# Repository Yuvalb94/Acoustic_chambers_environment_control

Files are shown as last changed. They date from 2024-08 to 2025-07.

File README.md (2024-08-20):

# Acoustic chamber environment control setup
In our experiments we house birds in acoustic chambers. These chambers include wide spectrum LEDs to mimmick sun light and a fan system to circulate fresh air in the chamber. Seasonal birds, like the canaries we study, are sensitive to the daily cycle of light and dark, the photoperiod, and to its changes as days grow longer in spring and grow shorter in autumn. To mimmick this in the acoustic chambers, we created the environment control and monitoring setup described in this repository. This setup, called *environmental system* and sketched in figure 1, controls the light switch in up to 8 acoustic chambers, monitors the light level, humidity, and temperature in a sentinel chamber, and monitors the weight of up to 8 birds using [in-house built scales](https://github.com/NeuralSyntaxLab/acoustic_chamber_environment_control/blob/scale_system_yc_version/scale_system_documentation/scale_design.md).
## System overview
Figure 2 shows the *environmental system*'s functional overview. The system is controlled by a python script running on a Raspberry Pi computer. [This script](https://github.com/NeuralSyntaxLab/acoustic_chamber_environment_control/blob/main/arduino_main.py) communicates with an Arduino microcontroller, which controls light switches, reads sensor data, and sends information back to the Raspberri Pi. 

The Raspberry Pi script:
 * Determines when lights should be turned on/off according to user-defined photoperiod regimes (detailed in [Operations](https://github.com/NeuralSyntaxLab/acoustic_chamber_environment_control/blob/scale_system_yc_version/README.md#operations)) and sends on/off commands to the Arduino.
 * Receives a sentinel chamber's temprature, humidity, and light sensor data from the Arduino and stores it and in .csv files.
 * Receives weight data of birds that are being monitored from the arduino and stores it (also in .csv files).
 * Store data locally and on the [storWIS drive](https://github.com/NeuralSyntaxLab/lab-handbook/wiki/Lab-Operations-and-Procedures#storwis) and/or send the data to the experimenter via Slack or Email.

Our environmental system allows flexibility in determining the photoperiod and its changes across days. Each  *environmental system* is given its unique ID. This allowes running experiments in different light cycles, or experiments on more than 8 acoustic chambers .

<figure>
 <br>
<figcaption> Figure 1: The environmental system setup </figcaption>
</figure>

---

## Table of contents
* **Part list** 
* **Preperations**
  1. [Setting up the Raspberri Pi](#setting-up-the-raspberry-pi)
  2. [Preparing hardware and connecting to Arduino](#preparing-hardware)
  3. [Setting up Arduino](#setting-up-arduino)
* **Operations**
  1. [Light control mode](#light-control-mode)
  2. [Light control & data acquisition mode](#light-control--data-acquisition-mode)

<br>

## Part list
[This table](https://github.com/NeuralSyntaxLab/acoustic_chamber_environment_control/blob/scale_system_yc_version/parts%20list.xlsx) contains the part list required to constructing one *environmental system*. The list reflects our current choice of microcontroller models, wiring, and connections. Many of these can be switched for the convenience of the user and their specific needs.

## Preperations
This section is a general overview of how to construct the *environmental system*. It contains links to separate manuals for manufacturing system components and describes how to connect them. This section also contains instructions about how to upload the Arduino code and how to calibrate the scale system. The next section, Opertaions, describes how to use the system once it's constructed and calibrated. 

### System hardware components
The following hardware components are constructed separately and wired after their installation in the acoustic chambers or in the experiment room's main instrumentation rack:
1. A Raspberry Pi minicomputer.
2. An Arduino Uno microcontroller.
3. Light control system - consists of 1 control box which connects to relay swiches on a maximum of 8 acoustic chambers.
4. Sensor box - consists of a humidity & temprature sensor (DHT) and a photoresistor (light sensor). Up to 1 box per setup.
5. Scale system - consists of 1 control box, capable of connecting up to 8 scales. Up to 1 system per setup.

To demonstrate the functional operation of the system, Figure 2 shows a simplified schematic that illustrates how sensors and actuators are connected to the Arduino microcontroller.
<figure>
  
  <br>
  <figcaption>Figure 2: Schematic diagram of the system components and their connections</figcaption>
</figure>

<br>
<br>
The following sequence of steps should be taken to construct the hardware components and to calibrate the system:

### 1. Set up the Raspberry Pi
When using a new Raspberry Pi, it has to undergo several steps, described in the [configuration guide](https://github.com/NeuralSyntaxLab/acoustic_chamber_environment_control/blob/cf7c2d09ca352680ac4c0b2b953d89da0c118fb5/User%20Guides/Raspberry%20Pi%20Configuration.md), before using it to operate the environmental system. 

If you are using an already used Raspberry Pi, move on to preparing the hardware.
Return to the [configuration guide](https://github.com/NeuralSyntaxLab/acoustic_chamber_environment_control/blob/cf7c2d09ca352680ac4c0b2b953d89da0c118fb5/User%20Guides/Raspberry%20Pi%20Configuration.md) if issues arise when running the `control_main.py` script.

### 2. Manufacture and prepare the light switches and sensor box 
This [assembly guide](https://github.com/NeuralSyntaxLab/acoustic_chamber_environment_control/blob/cf7c2d09ca352680ac4c0b2b953d89da0c118fb5/User%20Guides/Hardware%20Assembly%20Guide.md) contains a step-by-step manual explaining how to build each device.

* #### 2.1 The light control system
Figure 3a illustrates the light control system. The system contains relay switches to control the light in each acoustic chamber and a control hub-box (3b) that transmitts the Arduino command to all the individual switches. The hub-box contains two output ports on the short edge that are used to connect to the Arduino microcontroller and a 5V external power source. On the long edge on both sides are 8 output ports that can connect to the relay switches on the acoustic boxes. To connect each relay switch to the hub, construct the cable shown in Figure 3c.

<figure>
  <div style="display: flex; justify-content: space-around; align-items: center;">
    <div>
      
      <figcaption style="text-align: center;">3a; Light control system diagram</figcaption>
    </div>
    <div>
      <br>
      <br><figcaption style="text-align: center;">3b; Light control hub-box.<br>The Arduino port connects the signal circuit, which transmits the signal from the Arduino to all relay switches, along with a 'GND' connection. The 5V port connects to an external 5V power source that helps send voltage to the relay switches without overloading the Arduino microcontroller.</figcaption>
    </div>
    <div>
    <br>
    <br><figcaption style="text-align: center;">3c; Light control communication cable.<br>The cable is a simple 4-core cable with a 3-PIN Pigtail connector for easily connecting to the hub-box on one end, and a 3-pos connector to fit on the relay module on the other. In order to connect the relay switches on each acoustic box to the control hub, connect the relay-module end of the cable to the switch (as shown in the figure), spread the cable conveniently to the instrumentation rack and connect to one port of the hub-box.</figcaption>
    </div>
  </div>
</figure>

* #### 2.2 The sensor box
The sensor box should look like this: <br>
<figure>
   <br>
  <figcaption>Figure 4: The sensor box</figcaption>
</figure>
<br>

The box contains:

* DHT sensor (for detecting humidity, temprature)
* Photoresistor (for detecting light intensity)
* A connector for the communication cable (for receiving voltage - red and black wires, and sending data - green for DHT, white for photoresistor)

In order to connect the sensor box to the setup, construct the communication cable, shown in Figure 5 (guide for making the cable [here](https://github.com/NeuralSyntaxLab/acoustic_chamber_environment_control/blob/cf7c2d09ca352680ac4c0b2b953d89da0c118fb5/User%20Guides/Hardware%20Assembly%20Guide.md)).

<figure>
  <br>
  <figcaption>Figure 5: The cable for connecting the sensor box to the Arduino</figcaption>
</figure>

### 3. Manufacture and calibrate the scale system
The scale system allows to measure the weight of 8 birds simultaneously. This [Scale System setup guide](https://github.com/NeuralSyntaxLab/acoustic_chamber_environment_control/blob/7b98ca46d210fc865f576b8630c2cdef0f82fe2f/User%20Guides/Scaling%20System%20Setup%20Guide.md) explains how to build the system and how to calibrate the scales for getting precise measurements. **Note:** Calibrating the scale system requires connecting it the Arduino and running the Arduino code [described below](https://github.com/NeuralSyntaxLab/acoustic_chamber_environment_control/blob/scale_system_yc_version/README.md#5-set-up-the-arduino). 

Figure 6 illustrates the whole scale system. Similar to the light control system, it contains a control hub-box, which contains special breakout boards (Qwiic Scale NAU7802, Qwiic MUX) that helps transmit, amplify and convert the signal from up to 8 scales simultaneously. The Qwiic MUX board inside the hub-box connects to the Arduino microcontroller on one end, and the NAU7802 board connects to the eight input ports to which we can connect the scales with long communication cables.

<figure>
  <div style="display: flex; justify-content: space-around; align-items: center;">
    <div>
      
      <figcaption style="text-align: center;">6a; Scale system illustration.</figcaption>
    </div>
    <div>
      <br>
      <br><figcaption style="text-align: center;">6b; Scale system control hub-box.<br>The box contains the breakout boards that are connected to the Arduino and the docking ports. On the side of the box, channel numbers are marked for each port, so that it fits the channel on the Qwiic MUX that it is connected to.</figcaption>
    </div>
    <div>
    <br>
    <br><figcaption style="text-align: center;">6c; Scale system control communication cable.<br>The cable is a simple 4-core cable with a 4-PIN Pigtail connector for easily connecting to the hub-box on one end, and a 4-pos connector to connect to the scale on the other. In order to connect the scales to the control hub, connect the scale end of the cable to the scale, spread the cable conveniently to the instrumentation rack and connect to one port of the hub-box.</figcaption>
    </div>
    <div>
    <br>
    <br><figcaption style="text-align: center;">6d; The scale.</figcaption>
    </div>
  </div>
</figure>

### 4. Connect all the hardware to the Arduino
In order for the Arduino microcontroller to receive the data smoothely and without failtures, the devices must be connected properly. Figure 7 schematize the wiring diagram:
<figure>
  
  <figcaption>Figure 7: The systems's wiring diagram</figcaption>
</figure>
<br>

#### Wiring list 
The colors of the lines in Figure 7 refer to different lines in the cables connecting the devices to the Arduino according to the following wiring list. Each entry in the list is formatted as "Device wire ID (function in the device) - pin on Arduino":
1. To connect the light control system (2 wires):
   * Black (ground) - to any 'gnd'
   * White (signal) - to digital channel 13

2. To connect the sensor box (4 wires):
   * Black (ground) - to any 'gnd'
   * Red (voltage) - to 5V channel
   * White (photoresistor) - to analog channel A0
   * Green (DHT) - to digital channel 8

3. To connect the Scale System (4 wires):
   * Black (ground) - to any 'gnd'
   * Red (voltage) - to 3.3V channel
   * Yellow (signal) - to 'SCL' channel
   * Blue (signal) - to 'SDA' channel

### 5. Set up the Arduino
Before running the main script on the Raspberry Pi, make sure to load the appropriate code for the operation that you want on the Arduino.

1. Connect the Arduino to the Raspberri Pi with a USB-A to USB-B cable.
2. Open the relevant arduino code:
   * [arduino_code_0](https://github.com/NeuralSyntaxLab/acoustic_chamber_environment_control/blob/scale_system_add/arduino_codes/arduino_code_0/arduino_code_0.ino) - For light control only mode.
   * [arduino_code_1](https://github.com/NeuralSyntaxLab/acoustic_chamber_environment_control/blob/scale_system_add/arduino_codes/arduino_code_1/arduino_code_1.ino) - For light control & data analysis mode.
   * [arduino_code_2](https://github.com/NeuralSyntaxLab/acoustic_chamber_environment_control/blob/scale_system_add/arduino_codes/arduino_code_2/arduino_code_2.ino) - For initial set up and calibration of the Scale System.
3. Load the relevant code onto the Arduino using the IDE. (see instructions [here](https://docs.arduino.cc/learn/starting-guide/the-arduino-software-ide)).
4. Once all the hardware components are connected to the Arduino, open 'Serial Monitor' to check that the arduino operates smoothely, acquiring the neccesary data in every mode.

## Operations

$${\color{red}\text{Begin comment ********}}$$

*This section is organized in a difficult way. Specifically, the definition of operation modes and the definition of how to configure things are intermingled and this is too confusing. I suggest a different structure below*

$${\color{red}\text{End comment ********}}$$

### Operation overview
The *environmental system* can be used in two distinct *operation modes*:
1. Light cycle only - The system controls the light switches and does not read sensors. In this mode the system **TBD: Does it save data? Does it send data to the user?**
2. Light and sensors - The system controls the lights and also reads sensors.

The user chooses the operation mode by loading different codes to the Arduino and by manupulating a single configuration file on the Raspberri Pi. This section instructs how to run the system in example cases of the two operation modes. For the full information about how to use the configuration file see [this manual](https://github.com/NeuralSyntaxLab/acoustic_chamber_environment_control/blob/scale_system_add/config_files/How%20to%20use%20the%20config%20file.md).

### To start running the system

After creating the configuration file, the user needs to edit the `startup_script.sh` shell script and point to the full path of the configuration file by changing this line: <br>
`
py_script_name="$parent_path/control_main.py --config=/path/to/repo/acoustic_chamber_environment_control/config_files/config_file_name.yaml"
` 
<br> 

Editing the `startup_script.sh` shell script is needed since the system is set to execute it automatically on start-up. This prevents light cycle failues if the system accidently boots (e.g. after a power fluctuation) to ensure minimal disruption for the animals.

Then, to start running the *environmental system* the user can:

* Boot the Raspberri Pi.
* Alternatively,
  * Open a terminal on the Raspberri Pi.
  * Change the directory to the root directory of this repository.
  * Execute the shell script `startup_script.sh`

### Day to day operations
#### 1. Changing the light cycle
#### 2. Configuring the system's reports
#### 3. Housing a new bird
#### 4. Removing a bird

### Operation modes
### *The "Light cycle only" operation mode*
This is a minimalistic operation mode that allows using the setup only for controlling the light cycle. In this mode **TBD: what will be controlled? What sensors are registered? What data is saved and sent to user?**
To work in this mode:
1. Load the Arduino microcontroller with [arduino_code_0](https://github.com/NeuralSyntaxLab/acoustic_chamber_environment_control/blob/scale_system_add/arduino_codes/arduino_code_0/arduino_code_0.ino)
2. Edit the [config file](https://github.com/NeuralSyntaxLab/acoustic_chamber_environment_control/blob/scale_system_add/config_files/config_1.yaml): 
   * Write values in one of `sunrise` & `sunset`, `stable_date` or `days_offset` & `hours_offset` according to the [config file user manual](https://github.com/NeuralSyntaxLab/acoustic_chamber_environment_control/blob/scale_system_add/config_files/How%20to%20use%20the%20config%20file.md) in order to achieve the desired result.
   * Make sure that both `dataReadingAndSaving` values are 0.
3. Run the script.
4. See that it operates properly. The lights in the acoustc chambers should be turned on/off based on your parameter settings.<br>
The terminal should look like this:
$${\color{red}insert picture}$$

### The *Light and sensors* mode
In order to use the setup for data acquisition (sensor, weight), follow these instructions:
1. Load the Arduino microcontroller with [arduino_code_1](https://github.com/NeuralSyntaxLab/acoustic_chamber_environment_control/blob/scale_system_add/arduino_codes/arduino_code_1/arduino_code_1.ino).
2. Edit the [config file](https://github.com/NeuralSyntaxLab/acoustic_chamber_environment_control/blob/scale_system_add/config_files/config_1.yaml):
  * Edit light cycle parameters based on your needs.
  * For sensor data acquisition:
    * Set `sensorOutputBasePath` with the path to the output folder that will contain the sensor data, and make sure that the folder exists.
    * Set `sensorDataReadingAndSaving` to 1 
  * For weight data acquisition 
    * Set `scaleOutputBasePath` with the path to the output folder that will contain the scale data, and make sure that the folder exists.
    * Set `scaleDataReadingAndSaving` to 1
    * Determine the time when you want the daily weight report to be sent to slack in `sendWeightReportToSlackTime`
    * **IMPORTANT!** Enter the names of the birds that are being weighed in the channel number which their scale is connected to. The script will generate a folder for each bird in the scale output folder, in which their continuously accumulating weight report will be stored.
    * **MOST IMPORTANT!** Calibrate the scales:
      1. Exit the startup script and the running main control script. If there are birds in the chambers, make sure to temporary keep the lights in the acoustic boxes controlled by this setup in the correct on/off configuration manually, until the calibration proccess is over.
      2. Load Arduino with [arduino_code_2](https://github.com/NeuralSyntaxLab/acoustic_chamber_environment_control/blob/scale_system_add/arduino_codes/arduino_code_2/arduino_code_2.ino)
      3. On the Arduino IDE, click `Tools` -> `Serial Monitor` or click on the top right Serial Monitor logo.  
         When the serial monitor opens, it should immediately start communicating with the MUX system and notify the user with the status of every connected scale and instructions on how to calibrate. Be prepared with a calibrating item with known exact weight (preferably within a range of a few grams).
      4. Follow instructions on screen to calibrate the connected scales (see full calibration guide in the [Scale System setup guide](https://github.com/NeuralSyntaxLab/acoustic_chamber_environment_control/blob/cf7c2d09ca352680ac4c0b2b953d89da0c118fb5/User%20Guides/Scaling%20System%20Setup%20Guide.md).
      5. Once calibration is done, make sure to reload the [arduino_code_1](https://github.com/NeuralSyntaxLab/acoustic_chamber_environment_control/blob/scale_system_add/arduino_codes/arduino_code_1/arduino_code_1.ino) to the Arduino and then boot the system.

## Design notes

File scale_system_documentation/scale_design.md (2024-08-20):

Assembly1
01_Base
03_Pin
05_Weight

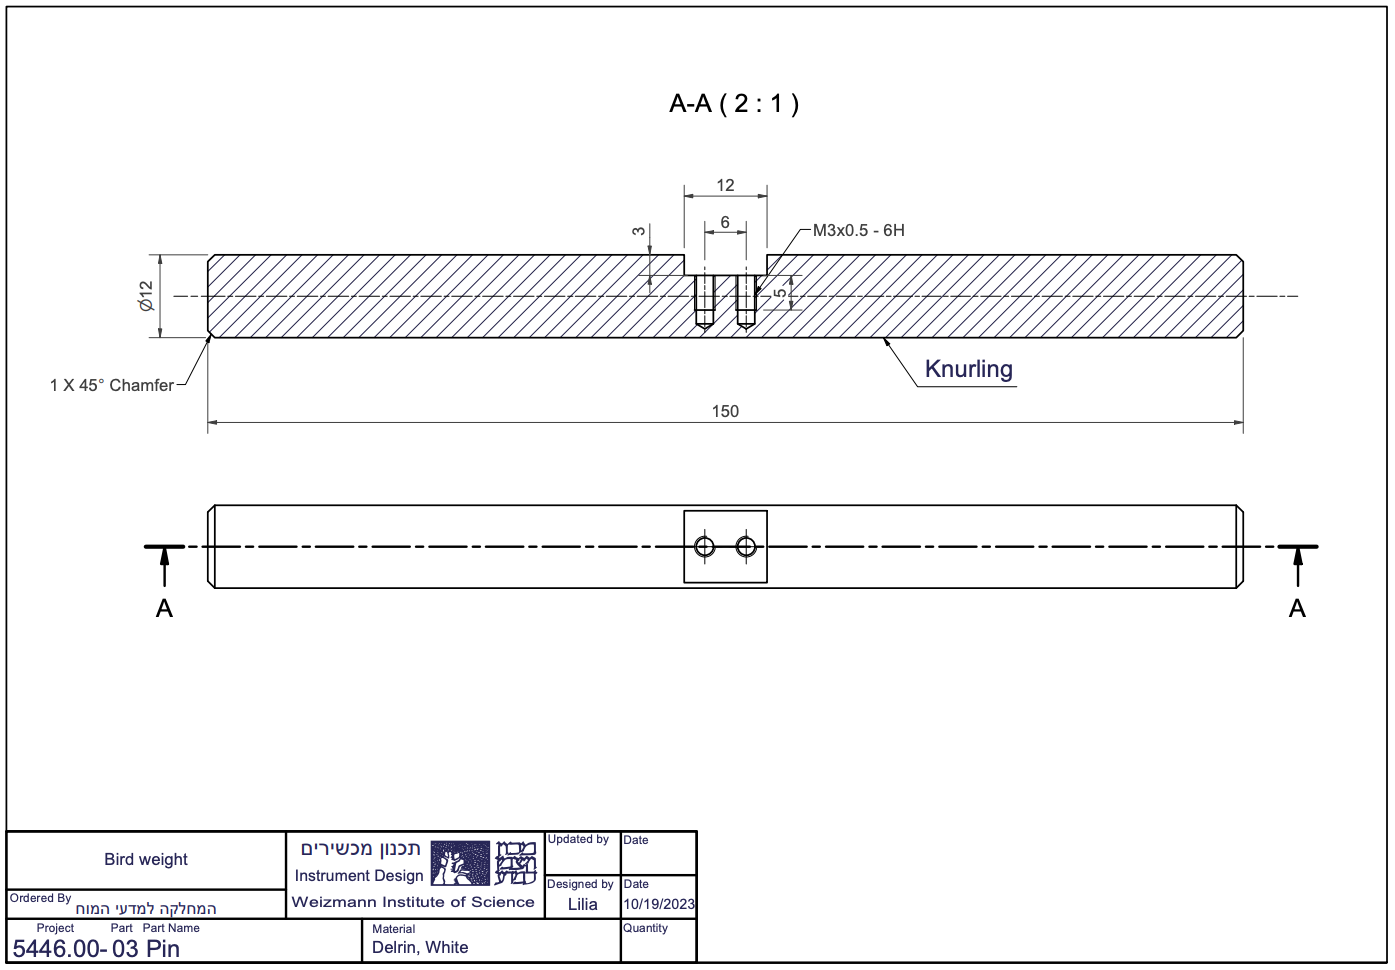
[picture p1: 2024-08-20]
scale_system_documentation/pngs/03_Pin.png

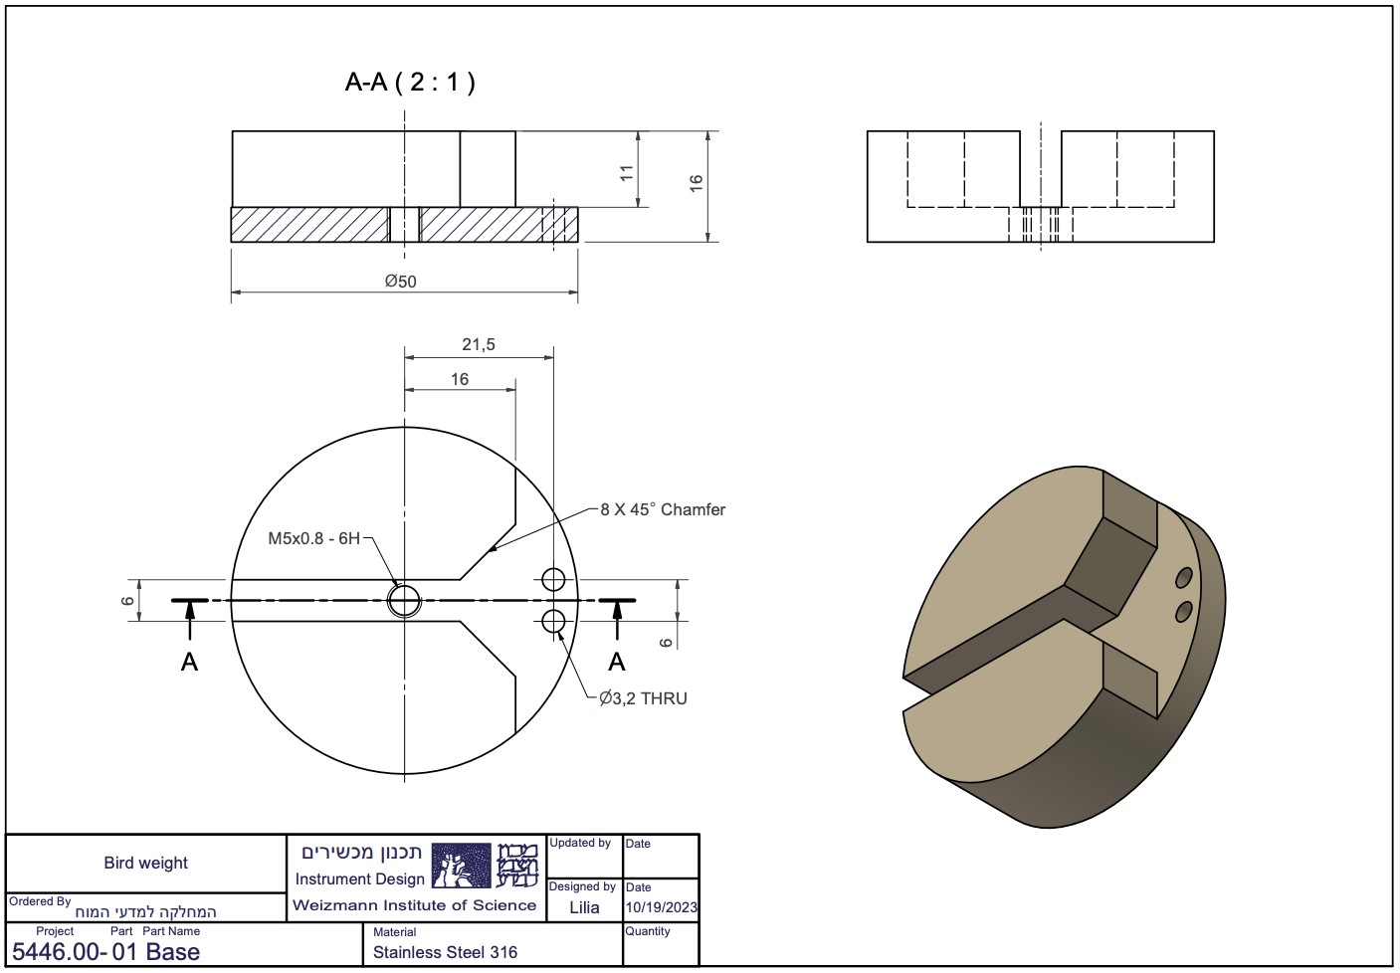
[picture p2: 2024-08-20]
scale_system_documentation/pngs/01_Base.png

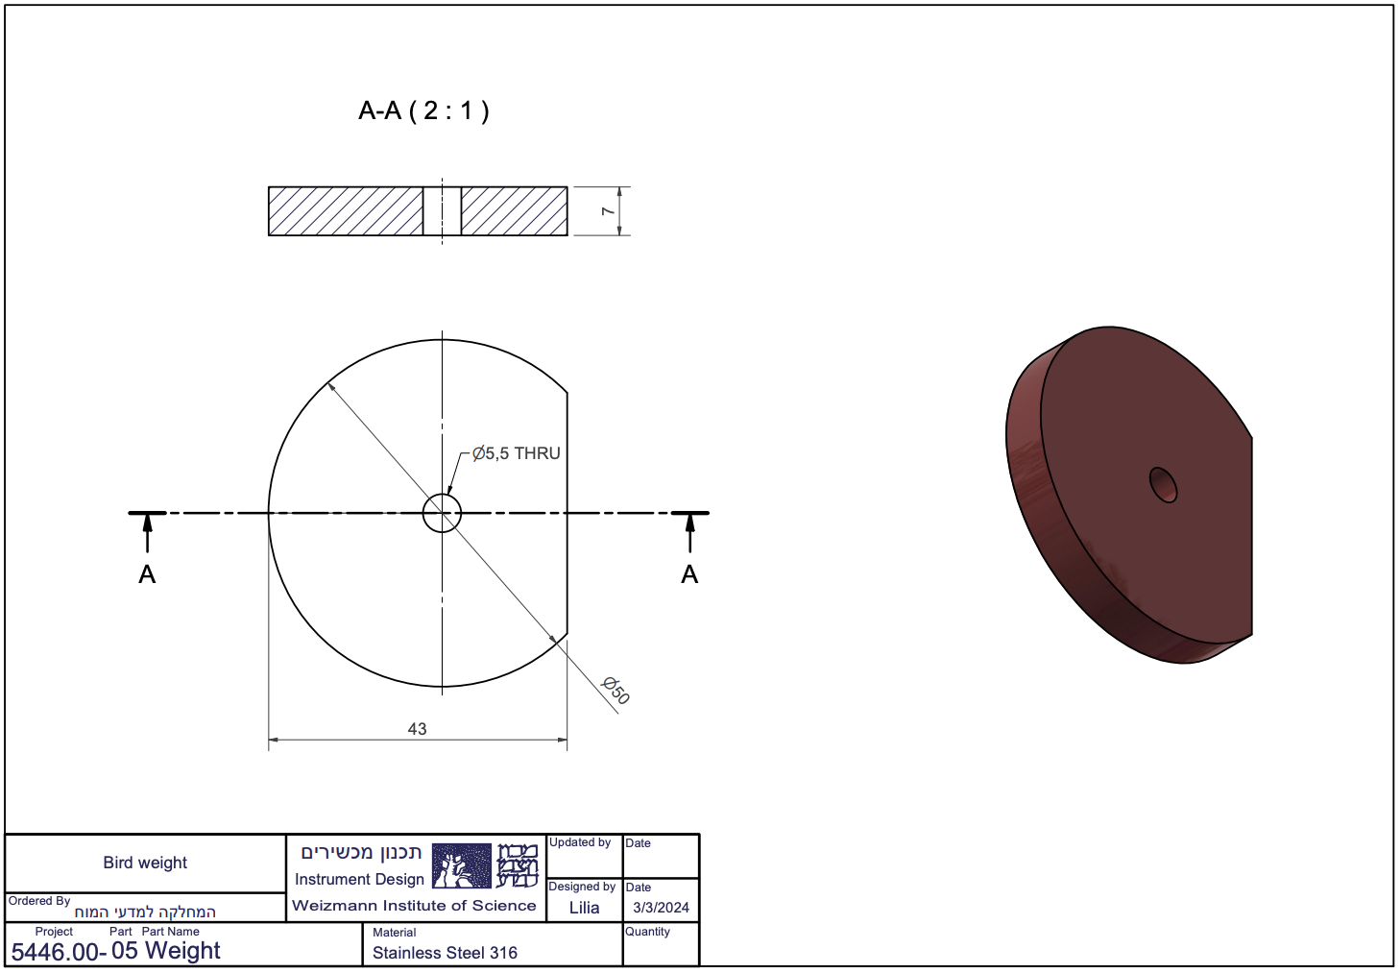
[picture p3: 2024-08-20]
scale_system_documentation/pngs/05_Weight.png

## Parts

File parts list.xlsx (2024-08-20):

part | URL | cost | notes
Light control system
Relay module 5Vdc 10A
4-Core electric cable
JST-SM Pigtail connector 3-PIN (male-to-female)
JST-SM Pigtail connector 2-PIN (male-to-female)
terminal block
5V, min.1A AC/DC power supply
Jumper wires
Plastic box
Sensor Box
DHT22 humidity & temprature sensor + analog sensor cable |  |  | cable should come with
light dependant resistor
10 kOhm resistor
JST-SM Pigtail connector 4-PIN (male-to-female)
4-Core electric cable
jumper wires
Plastic box
Scaling System
self-built scale:
mini load cell 500g straight bar
other parts …
Sparkfun Qwiic Scale NAU7802 breakout board (signal amplifier)
Sparkfun Qwiic MUX breakout board
4 Circuit Picoblade plug 425mm (male-to-female)
JST-SM Pigtail connector 4-PIN (male-to-female)
Flexible Qwiic cables
Flexible Qwiic breadboard cable
4-Core electric cable
Plastic box

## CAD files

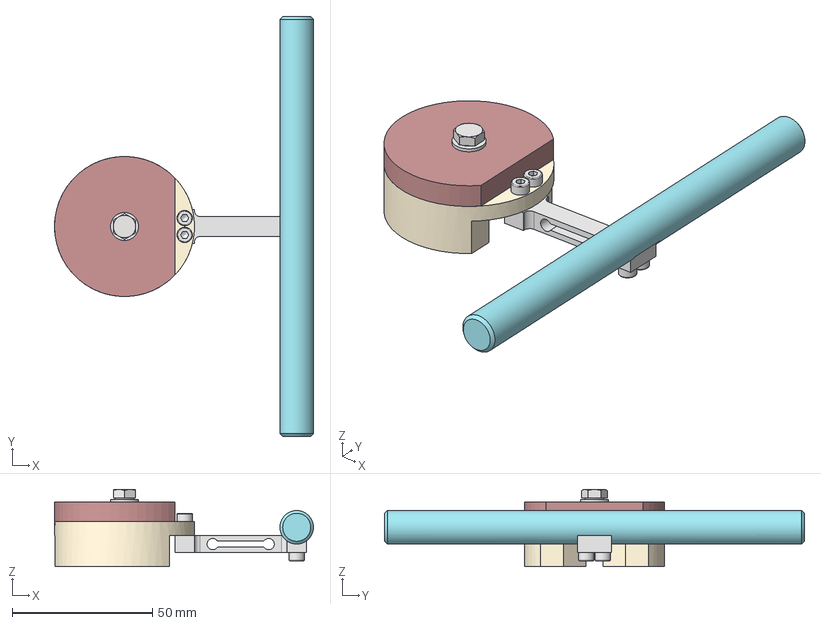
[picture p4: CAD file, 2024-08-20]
scale_system_documentation/Assembly1.stp
92.5 x 150.0 x 27.5 mm
Sensor
Base
Pin
ISO 4762 - M3 x 10 x 4
Weight
ISO 7089 - 5
ISO 4017 - M5 x 12

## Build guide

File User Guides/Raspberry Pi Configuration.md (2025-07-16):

# Setting up the Raspberry Pi
The Raspberry Pi is a minicomputer, on which we can run scripts that control our environmental system while also gathering important data. 
In order to use the Raspberry Pi for our purposes, we need to adjust some of its settings, install some files and libraries, and implement scripts that will run automatically when we want them to.

## Table of contents
1. [Installing the Raspberry Pi Operating system](#install-the-raspberry-pi-operating-system)
2. [Adding the Raspberry Pi to the WIS network](#adding-the-raspberry-pi-to-the-wis-network)
3. [Synchronizing the Raspberry Pi clock](#synchronizing-the-raspberry-pi-clock)
4. [Installing updates](#installing-updates)
5. [Mounting StorWis onto the Raspberry Pi](#mounting-storwis-onto-the-raspberry-pi)
6. [Acquiring neccesary files and libraries](#acquiring-neccesary-files-and-libraries)
7. [Manually running the script](#manually-running-the-script)
8. [Setting the script to run automatically when Raspberry Pi is turned on](#setting-the-script-to-run-automatically-when-raspberry-pi-is-turned-on)
9. [Copying data to the remote disk](#copying-data-to-the-remote-disk)

## Install the Raspberry Pi Operating system 
  Use [Raspberry Pi imager](https://www.raspberrypi.com/software/) to install the Rasraspberry pi OS (Legacy, 32 bit) operating system onto a compatible SD card.
  Set the user name to cohenlab and the password to the current lab user password.
  Now you can assemble the Raspberry Pi:  - insert the SD card in it's place, connect a keyboard, screen, mouse, ethernet, and power.

## Adding the Raspberry Pi to the WIS network
to connect to the Wis network and use storWis, we need to extract its MAC address and contact [Arthur Kalntarov](artur.kalantarov@weizmann.ac.il) to do that .
In terminal type:
```
ifconfig
```
Locate the MAC address in the first part of the text that opens (eth0). It is written after the word "ether" and has 6 pairs of characters separated by a colon(:).
Send it to Arthur and ask him to add it.
Once the Raspberry pi has been added, you will see on the top right corner of the screen next to the clock - two blue arrows pointing up and down, and it will display "eth0: configured".
Until this step is completed, you can continue with the following steps by connecting to the Wi-Fi, but you will not be able to connect to STORWIS, and the clock will not show the correct time (it's still OK to complete the steps in the sync clock procedure, but the clock might not show the exact time until you are connected to the network)

## Synchronizing the Raspberry Pi clock
  The Raspberry Pi clock uses the network to synchronize its clock. This is done by connecting to a server. The default server does not work properly. 
  So in this step, we will change the default server source. 
  Without a synchronized clock, we won't be able to install important updates and libraries which are essential.
  
Set the raspberry source as follows:
1. in the Raspberry Pi terminal type 
```
sudo nano /etc/apt/sources.list
```
2.  uncomment the bottom line 
3. In the file: change the mirror URL to a desired one (a list  of URLs is attached [here] (https://www.raspbian.org/RaspbianMirrors))
a mirror link has several components. Change only the existing  mirror URL (not the distribution or components)! 
```
deb http://<mirror-url>/ <distribution> <components>
```
for example:
```
deb http://raspbian.mirror.garr.it/mirrors/raspbian/raspbian/ bullseye main contrib non-free rpi

```
- mirror-URL: The URL of the mirror you want to use.
- distribution: The name of the distribution (e.g., stretch, buster, etc.).
- components: The software components you want to include (e.g., main, contrib, non-free, etc.).

4. Save and exit

## Installing updates 
Note that the last command in the code block below is the installation of the samba client which will allow us to connect to storWIS, and not a general update.
  Now run the following commands in the terminal.
  ```
  sudo apt-get update
  sudo apt-get upgrade 
  sudo apt-get install samba-common smbclient samba-common-bin smbclient  cifs-utils
  ```

## Mounting storWis onto the Raspberry Pi.
storWis is used to back up all the files which contain the environment monitoring data.
we can also access storWis relatively easily from different computers such that we have access to the data from any computer that is connected to the institute network.
 Create a credentials file, for instance, at the /home directory.
 Here, we will call it cred
The credential file is a text file containing the following format:
```
username=USERNAME(the desired username) 
password=PASWORD(its password) 
domain=wismain
```
Type in terminal:
```
sudo nano /etc/fstab
```
At the bottom of the file add the following line:
```
//isi.storwis.weizmann.ac.il/labs/cohen /mnt/path/to/mount/point cifs users,credentials=/PATH/to/cred,dir_mode=0777,file_mode=0777,noserverino,x-systemd.automount 0 0
```
Change the path to the mount point and to the credentials file. 

Save and exit

In terminal type
```
sudo mount -a
```
Now you should have Storwis folders in your directory, in the above example - /mnt. 

To check that the mounting was succesfull, you can type in the terminal either of the follwing commands:
```
df -h
```
In this example, look through the output to find your remote disk '//isi.storwis...' . It will be listed along with its mount point, which is the directory where it is mounted.

OR
```
ls /path/to/mount/point
```
In this example, the output should show all of the folders in the 'storwis' drive (see picture).

check_mounted_to_storwis

IMPORTANT: Storwis should be mounted only when the Raspberry Pi is connected to the internet!
If there is no internet connection and the script is trying to access / save files in the STORWIS directory, errors might occur. In order to avoid that, you can type the following command in the terminal:
```
sudo umount /mnt/path/to/mount/point 
```
The path to mount point should match the location you defined STORWIS to mount on in the previous step (in the example - /mnt)

## Acquiring neccesary files and libraries

* Download the [acoustic_chamber_environment_control](https://github.com/NeuralSyntaxLab/acoustic_chamber_environment_control/tree/main)  repository as by clicking on `Code > Download zip.` extract the zip file onto the dashboard.
  now you should have a folder by the same name containing all the repository content.

* Install all Python dependencies (by running `pip install -r path/to/requirements.txt`, or by installing all the libraries manually)
  Numpy should already be installed in the Raspberry Pi, but sometimes when installing pandas it messes up something with numpy and it has to be reinstalled. To do so run:
  ```
  sudo pip3 uninstall numpy
  ```
  And then when the process is complete, reinstall by running:
  ```
  sudo pip3 install numpy
  ```
  Using sudo will ensure that numpy will be available system-wide.
  
  If the problem presists (later, when you try to run the `control_main` script), you can also try fixing this problem by directly installing 'libopenblas':
  ```
   sudo apt install libopenblas-dev
  ```

* Install Arduino IDE: In terminal type `sudo apt-get install Arduino`.
* (OPTIONAL)Install visual studio code: In terminal type `sudo apt-get install code`.
* Install all Arduino dependencies: You can do so by looking them up in the libraries section of the Arduino IDE:
  1. DHT sensor library
  2. DHTlib
  3. SparkFun Qwiic Scale NAU7802 Arduino Library
  4. SparkFun I2C MUX Arduino Library
     
  OR - you can download the libraries directly from github as a .zip file and follow these instructions:  
    * In Arduino IDE go to `Sketch > Include Library > Add .ZIP Library` and choose the library file 

    * Scale libraries can be downloaded from [here](https://github.com/sparkfun/SparkFun_Qwiic_Scale_NAU7802_Arduino_Library) and [here](https://github.com/sparkfun/SparkFun_I2C_Mux_Arduino_Library). Temperature and humidity sensor library can be downloaded from [here](https://github.com/CainZ/DHT)  

## Setting the script to run automatically when Raspberry Pi is turned on
The script should be launched automatically when Raspberry Pi is turned on.

This is done using the following tools - 
1. We have a bash script, called `startup_script.sh` which is an infinite loop that keep relaunching the script and waits for it to finish. If it crashes, it's supposed to run again.
2. When Raspberry Pi turns on, we automatically run the `startup_script.sh` script.

To automatically run the script when the machine turns on - <br>
*remember to change the '/path/to/startup_script.sh' part with the actual path to the startup script where needed*
1. Modify the bash script permission. in Terminal type : `chmod +x path/to/script/startup_script.sh`. 
2. In terminal Type `sudo nano /etc/xdg/lxsession/LXDE-pi/autostart`
3. Add the following command to the end of the file - 
`@lxterminal -e /path/to/script/startup_script.sh`
  save and exit terminal.
4. Create a folder that will store the sensor data, and a folder that will store scale data. Update the path to those folders in the neccesary places according to the next step.
5. Update correct paths: Inside the acoustic_chamber_environment_control folder, there are several scripts, which use default paths that are not neccesarily compatible with the machine you are working on.
Update the paths in the following files:
 * in `startup_script.sh` -  update the path to config file.
 * in your [config file](https://github.com/NeuralSyntaxLab/acoustic_chamber_environment_control/blob/scale_system_add/config_files/cage_1_config.yaml), `dataOutputBasePath` and `scaleOutputBasePath` are the `base_path`'s to the folders you've created in the above step 4.

STILL IN WORK: AUTOMATICLLY SAVING THE DATA TO STORWIS
 * in [server_copy_script.sh](https://github.com/NeuralSyntaxLab/acoustic_chamber_environment_control/blob/main/server_copy_script.sh) update the `base_path` to the folder you've created in step 4.
Update the `base_server_path` to the path where you want to copy the data to (storWis path).

6. Reboot the machine to verify that it's working

## Copying data to the remote disk
**NOTE: This section is still in the making**
The script `server_copy_script.sh` is used to copy the output files that are created by our code to a remote disk.

For this to work, the disk must be mounted to the Raspberry Pi.

Once it's mounted, the copy job can be scheduled via crontab.

Generally speaking, we can work with crontab as follows -
1. Type `crontab -e`
2. Add a new line at the end of the file, following the crontab syntax (a very nice explanation is commented out in the file itself).
3. For example, we may add - `0 6 * * * /path/to/server_copy_script.sh` to run every day at 06:00

In our case, we need to add the following two lines to crontab - 
```
59 5 * * * chmod a+x /path/to/server_copy_script.sh
0 6 * * * /path/to/server_copy_script.sh
```

The first command will run at 05:59 and will verify that we have permission to execute the script.

The second command will run a minute later, 06:00, and perform the actual copy.

## Summary.
After you've completed all of the steps, you should have a fully functioning Raspberry Pi that, on start-up, launches a Python script that controls the Arduino microcontroller and reads data from it.
You also should have access to storWis, where .csv files will be copied automatically.
Follow the next steps to prepare the arduino and operate the setup according to your preferances.

# Check that the system was configures properly
After the Rasperry Pi waas configured by following all of the steps above, we can check that it works properly by first running the script manually:

## Manually running the script
1. Make sure you have updated the config file. You can use the first example [here](https://github.com/NeuralSyntaxLab/acoustic_chamber_environment_control/blob/f3f0723a57ecb227c9b016319a1390bf857777fb/config_files/How%20to%20use%20the%20config%20file.md)
2. Make sure you have a folder for output data files (according to what you specified in the config files, for the `dataOutputBasePath` and `scaleOutputBasePath` keys)
3. Open terminal and run `python /path/to/script/arduino_main.py --config=/path/to/config.yaml` (change path to script and config file accordingly)
4. The terminal should look like this:
   Terminal when running the script

*Replace photo with a similar one after making adjustments in the control_main.py script.

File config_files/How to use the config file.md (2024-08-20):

# Config file user manual
The [arduino_main.py](https://github.com/NeuralSyntaxLab/acoustic_chamber_environment_control/blob/main/arduino_main.py) code is used to control the acoustic chambers light cycle, and read data from the Arduino and write the date onto a '.csv' file. <br>
In order to easily manipulate between different operating options, we use a config file which helps define several parameters inside the script without having to visit the script itself and change it every time. <br>
The config file is saved in `.yaml` format, so that the paremeters inside are structured as `Key : Value`pairs seperated by a colon. See example [here](https://github.com/NeuralSyntaxLab/acoustic_chamber_environment_control/blob/main/config_files/cage_1_config.yaml) keys are on the left, values on the right.

There are a few things that we can manipulate by changing parameters in the config file:
1. Control the light cycle (when the lighs will be on/off)
2. Decide how to save data to the disk (sensor data / scale data / both, storage location)
3. Provide information about the scale system (what bird is monitored and in which channel)

## Controlling light cycle. 
By default, the system sets the light on/off times according to real-world sunrise and sunset times in our location (Weizmann), taken from `astral` library. Meaning that it will turn on the lights at the time of sunrise today in Weizmann, according to `astral`, and it will turn the lights off in sunset.

There are several ways to manipulate the acoustic chamber light cycle based on our research needs:
 1. **Set sunset time and sunrise time manually** - you decide by yourself when the light will be switched on/off.
 2. **According to a stable date** - set a fixed date for which sunrise and sunset times will be calculated and won't change.
 3. **According to day offset** - sunrise and sunset times will be calculated according to the number of days drift from today. For instance, if today is 16.07.2024 and you've passed `-10 days`, then sunrise and sunset times will be calculated according to 06.07.2024. The next day, sunrise and sunset  will be calculated according to the 07.07.2024. If you pass 0 in the days offset option, sunrise and sunset times will be calculated according to today's times, without any drift. If you want to control the light according to a future date, for instance, plus 10 days from 16.07.2024, then just pass `10` in the days offset key in the config file.

NOTE! It is important to write the hours / dates in a specific format (examples given below).

   ### Hirerchy of light cycle control options
The main script running on the Raspberry Pi is programmed to determine the light cycly times according to the first given input (manual -> fixed date -> days offset). Meaning that if a manual sunrise and sunset times are given, it will set the cycle based on those times and ignore the other values (fixed date, days offset). If the user does not write anything in the `sunrise` and `sunset` keys, the script will go on to the next level of `fixed date`, and if it is empty as well, it will go next to `days/hours offset`. If `days offset` and `hour offset` are both 0, the script will use the default values. <br>

**NOTE! if the user chooses not to manipulate the sunrise and sunset times, The `days offset` and `hours_offset` keys must get the value 0, or the script will collapse!**

## Config file format
The Python script expects a specific value format. Thus, it is essential to be consistent and precise when updating values to prevent the script from crashing. You don't need to change the critical format.
Example YAML file

```yaml
room_name: BigRecRoom 
env_system: 1
sunrise:  #time format should be as follows 'h:m' for instance 5:45:21 or 21:6 (which will give you 21:06:00) never put a zero before a number as in 05:06, just write 5:6 note, don't enter seconds!
sunset:  
stable_date:  # the date should be in the following format : 'yyyy/mm/dd', i.e. '2022/01/02' 
days_offset: 0
Hours_offset: 0
dataOutputBasePath: /Users/cohenlab/Desktop/scale_test_control/arduinoData
sensorDataReadingAndSaving: 1
scaleOutputBasePath: /Users/cohenlab/Desktop/scale_test_control/scaleData
scaleDataReadingAndSaving: 1
sendWeightReportToSlackTime: '12:05'
# CHANNELS 1-8: enter the name of the bird connected to each MUX channel. This will be used to create a folder for each bird and store its weight report. Leave non-connected channels empty.
channel0: 'testy'
channel1: 
channel2: 
channel3: 
channel4: 
channel5: 
channel6: 
channel7:

``` 
* `room_name`  - The room in which this environmental system is in (Big/Small_RecRoom)
* `env_system` - The ID of the environmental system (single control setup connected to up to 8 boxes)
* `sunrise` and `sunset` - These are the manual options to set the light cycle. Note: time format should be as follows 'h:m' for instance, 5:45:21 or 21:6 (which will give you 21:06:00). Do not put a zero before a single digit hour/minute time marker, as in 05:06. Just write 5:6. 
* `stable date` - The date according to which the light cycle times will be calculated. The date should be in the following format: 'yyyymmdd', i.e. '20220102'. This is the second of January 2022, 2.1.2022. Remember to pass the data as a string
* `days_offset` - The number of days offset from today. Enter a negative or positive number to manipulate, or 0 to stay in default mode. Note! if other paraeters are not defined, this key cannot stay empty - for default mode user nust enter 0 or the script will crash!
* `hours_offset` - Similar to days offset but for hours.
* `dataOutputBasePath` - The path to the folder where **sensor** data will be stored.
* `sensorDataReadingAndSaving` - Decide if you want to record and save **sensor** data or not. choose 1 for yes, and 0 for no.
* `scaleOutputBasePath` - The path to the folder where **scale** data will be stored.
* `scaleDataReadingAndSaving` - Decide if you want to record and save **scale** data or not. choose 1 for yes, and 0 for no.
* `sendWeightReportToSlackTime` - Define the time of day ('HH:MM') you want the daily weight report for each monitored bird to be sent to slack, if you chose to record and save scale data.
* `channels 1-8` - For every channel of the MUX scale system, write the name of the bird that is monitored as a string. Leave non-connected channels empty / null.
 
## Example config files
* First example: sunrise and sunset times will be calculated according to stable_date and data won't be read and saved.
```yaml
room_name: BigRecRoom 
env_system: 1
sunrise:  #time format should be as follows 'h:m' for instance 5:45:21 or 21:6 (which will give you 21:06:00) never put a zero before a number as in 05:06, just write 5:6 note, don't enter seconds!
sunset:  
stable_date: '2024/06/21' # the date should be in the following format : 'yyyy/mm/dd', i.e. '2022/01/02' 
days_offset: 0
Hours_offset: 0
sensorOutputBasePath: 
sensorDataReadingAndSaving: 0
scaleOutputBasePath: 
scaleDataReadingAndSaving: 0
sendWeightReportToSlackTime: 
# CHANNELS 1-8: enter the name of the bird connected to each MUX channel. This will be used to create a folder for each bird and store its weight report. Leave non-connected channels empty.
channel0: 
channel1: 
channel2: 
channel3: 
channel4: 
channel5: 
channel6: 
channel7:

``` 

* second example: Light cycle times will be calculated according to 25 days and 2 hours drift from today, sensor data will be saved at `/home/desktopArduinoData`, scale data will not be saved, therefore it does not matter what the user writes in `sendWeightReportToSlackTime` and `channels 1-8`.
```yaml
room_name: BigRecRoom 
env_system: 1
sunrise:  #time format should be as follows 'h:m' for instance 5:45:21 or 21:6 (which will give you 21:06:00) never put a zero before a number as in 05:06, just write 5:6 note, don't enter seconds!
sunset:  
stable_date:  # the date should be in the following format : 'yyyy/mm/dd', i.e. '2022/01/02' 
days_offset: 25
Hours_offset: 2
sensorOutputBasePath: `/home/desktop/ArduinoData`
sensorDataReadingAndSaving: 1
scaleOutputBasePath: 
scaleDataReadingAndSaving: 0
sendWeightReportToSlackTime: '30:89'
# CHANNELS 1-8: enter the name of the bird connected to each MUX channel. This will be used to create a folder for each bird and store its weight report. Leave non-connected channels empty.
channel0: 'jokesonyou'
channel1: 
channel2: 
channel3: 
channel4: 
channel5: 
channel6: 'doNotReplyRb17'
channel7:

``` 

* third example: Light cycle times will be calculated by manual setting to turn on at 7:25AM and turn off at 18:30PM, although `stable_date` and `days_offset` are holding valid values (Hierarchy). In addition, sensor data will be saved at `/home/desktop/ArduinoData/SensorData`, and scale data for birds 'lbrb43', 'rb100', 'lpnkrg1' will be recorded and saved at `/home/desktop/ArduinoData/ScaleData`. Once a day in 10:00 AM a daily report containing all data recorded for each bird so far, will be sent to `monitor alerts` group in slack as a .csv file.
```yaml
room_name: BigRecRoom 
env_system: 1
sunrise: '7:25' #time format should be as follows 'h:m' for instance 5:45:21 or 21:6 (which will give you 21:06:00) never put a zero before a number as in 05:06, just write 5:6 note, don't enter seconds!
sunset: '18:30'
stable_date:  # the date should be in the following format : 'yyyy/mm/dd', i.e. '2022/01/02' 
days_offset: 25
Hours_offset: 0
sensorOutputBasePath: `/home/desktop/ArduinoData/SensorData`
sensorDataReadingAndSaving: 1
scaleOutputBasePath: `/home/desktop/ArduinoData/ScaleData`
scaleDataReadingAndSaving: 1
sendWeightReportToSlackTime: '10:00'
# CHANNELS 1-8: enter the name of the bird connected to each MUX channel. This will be used to create a folder for each bird and store its weight report. Leave non-connected channels empty.
channel0: 'lbrb43'
channel1: 'rb100'
channel2: 
channel3: 
channel4: 'lpnkrg1'
channel5: 
channel6: 
channel7:

```

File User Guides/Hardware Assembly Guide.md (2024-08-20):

Since we are responsible for the well-being of the labs, we aim to monitor and control different aspects of the bird environment. Controlling light cycles can directly affect the bird's singing.
As part of monitoring and controlling the acoustic chamber environment, we use several components connected to an Arduino microcontroller controlled by a Raspberry Pi unit. 
We monitor temperature, humidity, light intensity, and bird's weight and control light cycles within the acoustic chamber.

To monitor the chamber environment and control its light cycle,  Several components are connected to the Arduino: 

 * [DHT22 Temperature and humidity sensor](https://il.farnell.com/dfrobot/sen0137/dht22-temp-humidity-sensor-arduino/dp/3517874) - a digital component outputs a digital signal. 
 * [A light-dependent resistor](https://il.farnell.com/advanced-photonix/norps-12/light-dependent-resistor-1mohm/dp/327700?st=327700) -  an analog component connected in series with a resistor. Outputs an analog signal. 
 * [A 5V trigger relay module](https://il.farnell.com/mcm/83-17990/5v-trigger-relay-module-for-arduinoraspberry/dp/2801412?st=2801412) - receives a digital input turning on /off the light inside the acoustic chamber. 
 * A [Qwiic scale amplifier](https://www.sparkfun.com/products/15242) and a [500g mini load cell straight bar](https://www.digikey.co.il/en/products/detail/sparkfun-electronics/SEN-14728/9555602?s=N4IgTCBcDaILIEkByCAEAZA8gQQCKoGEBRddVAVgAZKBxVAZQBUAlbBGgCUdQCFtmQAXQC%252525252BQA) - this components serve as a scale to measure birds weight.

Every acoustic chamber has a relay module controlling the chamber's light cycle.
Except for the trigger relay module, the rest of the sensors are assembled in a box placed inside the acoustic chamber and connected to the Arduino via a [9-pin D-Sub](https://www.digikey.co.il/he/products/detail/mikroelektronika/MIKROE-2092/5804553?s=N4IgTCBcDaILIEkDSAlA8gUQLRgAwE4IBdAXyA) cable and a [connector](https://www.digikey.co.il/he/products/detail/assmann-wsw-components/A-DF-09-LL-Z/5051922).

# Sensor box

## Components and tools for sensor box assembly:
 * DHT22 temperature and humidity sensor.
 * Light-dependent resistor (LDR).
 * 10 kilo-ohm resistor. 
 * A plastic box ([this for example](https://www.digikey.co.il/he/products/detail/bud-industries/CU-1943/439229))
 * Qwiic scale amplifier
 * 500g mini load cell straight bar
 * 9 pin D-Sub cable
 * 9 pin D-Sub connector and compatible nuts and bolts(usually 3m size is sufficient)
 * Jumper wires
 * Holdering station
 * Hot glue gun
 * A tool to make holes in the plastic box (I used a soldering pencil, not from the soldering station!)
 * A multimeter
 * An electrical type (such as isolierband)

## Sensor box assembly
  * Make a small hole for the light-dependent resistor cable in the box lid.
  * Make a circular hole for the light-dependent resistor.
  * Make a small hole for the mini-load cell cables. 

Glued sensors onto the box with:


* Glue  the temperature and humidity sensor and the light-dependent resistor onto the box lid (as in the picture above)

* Make a hole for the D-Sub connector on the side of the box.

D-Sub connector connections:


* If you have a male D-Sub connector, cut the male side of your D-Sub cable and expose its wires, or vice versa if you have a female D-Sub connector.

* Connect the D-Sub connector to the compatible side of the cable. At the connector back (the side that is not connected to the cable), there are 9 
  numbered soldering cups. 
  Using the multimeter, identify which soldering cup is connected to which exposed cable. 
  For example, touch the red wire with one end of the multimeter and the soldering cup with the other. If the multimeter made a bip sound, this means they 
  are connected.  

* Identify the soldering cup that is connected to the red D-Sub wire. This will be connected to the 5V input.
* Identify the soldering cup that is connected to the Black D-Sub wire. This will be connected to the ground input.

* Solder one leg of the LDR to one leg of the 10kohm resistor. This will be the output leg. Solder the other leg of the LDR to 5V input and the other leg of the 10 Kohm resistor to ground. As in the picture below


 *  Using the multimeter, identify a soldering cup and its corresponding D-Sub wire (for example, green wire to cup number 2). Solder the output leg to an individual cup. This will be connected to Arduino pin A0 via the D-Sub cable.
 * The [DHT22 sensor](https://il.farnell.com/dfrobot/sen0137/dht22-temp-humidity-sensor-arduino/dp/3517874), has a connector of itself, and it comes with 
  a specific cable with red (5V input), black (ground input) and green (digital output) wires.As in the picture below :


 * Solder the DHT22 red  wire to the 5V input, solder the DHT22 black wire to the ground input, and solder the green wire to a desired soldering cup (Note! identify which is the corresponding D-Sub wire). This digital input for the temperature and humidity sensor will connect to Arduino pin 8.
   
 * Preparing the Qwiic scale amplifier: Solder Four 90-degree legs to each of the four following inputs: 1.GND 2.3V3 3.SDA 4.SCL  (can also be done with soldering of jumper wires directly to the amplifier). Glue the amplifier to the bottom of the box.


  * Solder the GND amplifier input to ground.
  * Solder the 3v3 input to an individual solder cup (Note! Identify which is the corresponding D-Sub wire).
  * Solder the SDA  output to an individual solder cup (Note! Identify which is the corresponding D-Sub wire).
  * Solder the SCL  output to an individual solder cup (Note! Identify which is the corresponding D-Sub wire).

* Pass the mini-load cell cables through the hole you made earlier and connect them to the Qwiic scale amplifier using the green, built-in clips on the amplifier. As in the picture below
 
    

* After you've finished soldering, make sure to cover every conducting part with electrical type.
* Push the D-Sub connector into its hole in the box (the one that you passed wired through, as in the picture).
  

* To each identified wire(wires which you know soldered to their corresponding solder cups), solder jumper wire that will fit the Arduino pins. similar to the picture below (Note, the wires are not fully assembled in that picture)

   

* Place the sensor box inside the acoustic chamber and pass the D-Sub cable through the hole in the left side of the chamber.

  # 5V trigger relay module (light switch)

  ## Components and tools for 5V trigger relay module:
   * 5V trigger relay module.
   * Screwdrivers (regular and small for electronics).
   * Hot glue gun.
   * An electrical type (such as isolierband).
   * 20cm power cable (with two exposed sides).
   * Wire stripper.
   * Permanent marker.
   * Power drill.
   * Terminal connector  : 
   * Cutter.

   ### Light switch assembly
  * Power connection and switches are at the right side of the acoustic chamber(if you are standing in front of its door). Check that ventilation (top switch indicated with blue LED) and light (bottom switch indicated with red LED) work properly.
  * Disconnect the power cord from the acoustic box, and disassemble the switch panel on the right of the acoustic chamber by unscrewing the top and bottom screws.
    
  * Mark the bottom white wire(in the picture, it is marked  with red, and it's the rightmost wire). As in the picture above, there are 6 cables: 2 blue, 3 white(the rightmost wire is white but colored with red), and 1 red cable. The ventilation switch is connected with blue, red, and white wires. The light switch is connected with 1 blue and 2 white wires.
  * Cut both light switch white wires(the one you have marked and the one adjacent to it)
  * Expose all of the white ends, two of  which have legs and are connected to the switch and two of which are coming out of the box.
  * Cut one of the 3 wires in the exposed power cord on both sides and expose the two  remaining wires such that you'll have conductive wire exposed.
  * Connect each of the  two exposed white wires from the box to the terminal connector.On the other side of the terminal connector, connect one leged white cable with one of the exposed power cord wires and do the same with the remaining power cord and legged white wire, as in the pictures below:

       
       
       white cable marked red is connected together with the blue power cord wire at one end of the terminal connector. The other side is connected to the box. The other white-legged wire is connected together with the brown power cord cable.

* Connect the two power cord exposed wires to the ON inputs in the power resistor. one wire in the middle and the other at the top  left side (according to the picture below).
  
    

* Secure the power cord and its connected switch on top of the acoustic chamber using a type 
* Connect the three legs on the right side (according to the picture above) to the Arduino, to their signs: plus sign to 5V, minus sign to ground, and S - signs signal; this should be connected to Arduino pin 13.

# Arduino pinout 
This will describe to which pin each component should be connected, according to [This Code](https://github.com/NeuralSyntaxLab/acoustic_chamber_environment_control/blob/main/arduino_code/arduino_code.ino).

 * Light-dependent resistor - Arduino pin A0. Should also be connected to 5V and ground
 * Temperature and humidity sensor Arduino pin 8. Should also be connected to 5V and ground
 * Relay trigger module - Arduino pin 13. Should also be connected to 5V and ground
 * Qwiic scale amplifier  - Arduino pins SDA and SCL (according to markings on the amplifier). Should also be connected to 3V3 and ground.

# Scale System
## 1. Self-built weighing device (scale)
The self-build scale consists of the following items:
* Mini load cell 500g
* 3D printed perch, customized to be screwed onto the load cell
* Cylindrical steel weight, also customized to screw the load cell onto it
* 4-pin connector, to easily connect and disconnect the scale to/from the control system (for example - [Circuit Picoblade Male-to-Female plug 425mm (multiple)](link))

see [scale design](https://github.com/NeuralSyntaxLab/acoustic_chamber_environment_control/tree/0fc50bf446f8784b286c2851cd4cca4fbe7e9609/scale_system_documentation) for further information and specifics.

To asemble the scale:
1. Solder the wires of the load cell to a 4-pin connector
2. Screw the load cell to the 3D printed perch on one side and to the steel weight on the other side, making sure that:
   * The side with the wires is screwed to the weight, enabling the wires to go in the gap under the weight.
   * The load cell's arrow indicating its direction is pointing down.

 <br>



## 2. Control box
When weighing several birds in one setup, it is highly recommended to use a central control system, so that the microcontroller and minicomputer are located in a central, organized location, and the scales are connected through a contro box located next to them. This control box contains the breakout boards (MUX, NAU7802) with customized connectors to easily modify the connections with the scales scattered around the room inside the birdcages. 

**Part list:**
1. Plastic box
2. SparkFun Qwiic MUX breakout
3. SparkFun QwiicScale NAU7802 (multiple)
4. JST-SM Pigtail connector (4-PIN) (multiple)
5. Flexible Qwiic cables (multiple)
6. Flexible Qwiic breadboard cable

It should look like this: <br>

 <br>

## 3. Communication cables
In order to easily manage connecting the scales to the control system, it is best to make custom communication cables with the neccesary length to connect between the location of the bird cage and the control box using simple 4-core network/telephone cables. These cables connect to the scale on one side (directly, or using the same connector used for the load cell), and to the NAU7802 breakout board on the other side. These cables allow easy setup and removal of the scale in and out of the birdcage, inside the acoustic box.



ADD SCHEMATIC DIAGRAM - with JSM Pigtail connector, cable, and Picoblade connector.

##s 4. Overview

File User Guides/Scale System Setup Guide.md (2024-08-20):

# Scale System setup guide
## 1. Overview
The Scale System is a setup designed to monitor the weight of multipe, freely-behaving birds directly while in their cage (possibly while recording the birds' songs, monitoring their movement or recording neural data directly from their brain), in order to detect weight loss as a marker for their health condition.

The weighing is conducted by placing a load-cell-based weighing device (scale) in the bird's cage. This device is connected to an ADC breakout board (NAU7802) which helps convert and amplify the signal from the load cell to an I2C signal, readable with a microcontroller from which we can extract the weight in grams. The data collection is controlled by a script that runs continuously on the minicomputer, receives weighing data from the microcontroller, and stores it in '.csv' files.

Each Scale System is capable of connecting up to 8 weighing devices per microcontroller with the help of another breakout board (MUX), which enables communication with multiple I2C devices simultaneously.

## 2. Part list
The Scale System consists of the following items:
  1. Raspberry Pi (or similar) minicomputer
  2. Arduino UNO microcontroller
  3. Control box
      1. Sparkfun Qwiic MUX breakout board
      2. Sparkfun Qwiic Scale NAU7802 breakout board (multiple)
      3. Flexible Qwiic cables 
      4. Docking points (4-PIN JSM-ST Pigtail connector - male, multiple)
  4. Self-built weighing devices (multiple)
     1. Mini load cell 500g
     2. 3D printed perch, customized to be screwed onto the load cell
     3. Cylindrical steel weight, also customized to screw the load cell onto it
     4. 4-pin connector, to easily connect and disconnect the scale to/from the control system (for example - [Circuit Picoblade Male-to-Female plug 425mm (multiple)](link))
  5. Communication cables
     1. 4-PIN JSM-ST Pigtail connector (female)
     2. Circuit Picoblade Male-to-Female plug 425mm

see [general part list](link) for full list of parts and where to get them.

### Scale System setup schematic overview

 <br>

### Assembly
See [Scale System assembly guide](link) for assembly instructions for each part.

## 3. Wiring the Scale System 

Before operating the Scale System setup, follow these instructions to connect all the pieces together:
1. Open the control box, and connect as many docking points (NAU7802 board + Pigtail connector male) to the MUX as you plan to use (When adding/removig scales at any point, it will be neccesary to stop the main script, open the box and re-wire the docking points. NAU7802 boards that are connected to the MUX but not to a scale can cause issues with the code). Write down under each docking point to which channel on the MUX board it is connected to.
2. Place scales in the corner of the cages of the birds you wish to weigh with their connector sticking out.
3. Connect the communication cable to the scale inside the acoustic box and spread the cable through the hole in the side of the acoustic box all the way to the control center (Repeat for all scales you wish to connect)
4. Connect the communication cable's other side to a docking point on the control box. IMPORTANT! make sure that you know which bird is connected to which channel on the control box (and MUX accordingly)
5. Connect the Qwiic MUX to the Arduino microcontroller through the hole in the control box lid, using a Flexible Qwiic breadboard cable (connector on one side and 4 separate pins on the other):
  * Black pin (ground) - to any 'gnd'
  * Red pin (voltage) - to 3.3V channel
  * Yellow pin (signal) - to 'SCL' channel
  * Blue pin (signal) - to 'SDA' channel

 <br>

6. Connect the Arduino microcontroller to the minicomputer.
7. Connect the minicomputer to the power source, screen, keyboard and mouse. Continue to the next step to operate the system on the minicomputer.

## 4. Operating the system
Once the system is up and connected, wait for the minicomputer to start up and follow the instructions:

### 1. Calibrating the scales
1. Exit the automaticly-started control script.
2. Load Arduino with [arduino_code_2](https://github.com/NeuralSyntaxLab/acoustic_chamber_environment_control/blob/scale_system_add/arduino_codes/arduino_code_2/arduino_code_2.ino) (see instructions [here](https://docs.arduino.cc/learn/starting-guide/the-arduino-software-ide)).
3. Open the Serial Monitor: <br>
On the Arduino IDE, click `Tools` -> `Serial Monitor` or click on the top right Serial Monitor logo.  
When the serial monitor opens, it should immediately start communicating with the MUX system and notify the user with the satatus of every connected scale and instructions on how to calibrate. Be prepared with a calibrating item with known exact weight (preferably within a range of a few grams).

* In general, output on the serial monitor will show detected scales and their calibration values (zero-offset and calibration factor) in the setup phase.
* A scale is detected on channel X if a docking port (NAU7802 board) is connected to that channel on the MUX board.
* After the setup phase, a new line of data from all 8 channels is given every second in the format `c0: 0.00` for channel 0, `ch1: 2.14` for channel 2 and so on.
* Some disconnected channels give numbers that are not 0 or none because the Arduino already has information about previous scales that were connected to those channels stored in its memory. Just ignore them and only look for the relevant channels.
* At Initial setup of a new Arduino, scales should not have calibration values, and you will have to follow the on-screen instructions in the serial monitor and calibrate each connected scale.
* For every change - relocation, addition ,cleaning of a scale etc. - **re-calibration of the scale is neccesary.**

4. Wait for the setup phase to complete, click on the Message panel to pass input to the Arduino, write `c` and press enter. Calibration process will now begin and indicative prompts will appear.
  * At initial setup, the Arduino will not detect calibration values for any scale and calibration proces will start automatically!

5. Follow instructions on screen to complete the calibration process for the desired scales (for more information see [arduino code guide](https://github.com/NeuralSyntaxLab/acoustic_chamber_environment_control/blob/9a08e14dcccb3a1217388fe7d782128831e4b6a5/arduino_codes/Arduino%20code%20guide.md)).

#### Example 1: Calibrating in and already-used setup, but with new scale wiring


In this example, the first lines show that docking ports 0 and 6 are "active" (meaning that they are connected to the MUX board). Other ports / channels are not detected because they are not connected to the MUX board. The output will include the zero offset and calibration factor that are saved on the Arduino memory for these ports. 
After the setup phase in which the Arduino passed information about channels 0 and 6, it moves on to the next phase. 
Now every second a new line of data is given. We can see that it is a used setup because weighing data is given for disconnected scales. We will focus on data given from channels 0 and 6.

#### Calibration process for scale 0 looks like this:

Arduino IDE calibration example 1_2

1. After entering `c` in the message panel, the calibration began and the first prompt was given.
2. User input was 0 - to calibrate scale on port 0.
3. Next prompt instructed to clear the scale from any weight and press any key to continue - in this case the user input was `k` (could be any key).
4. Next prompt indicated the new zero offset saved to the Arduino memory.
5. Next prompt instructed to put known weight on the scale and press any key. In this case user put a known weight of 2.14 grams on the scale, wrote `k` in the message panel and pressed enter.
6. Next prompt instructed to enter the known weight in grams in the message pael and press enter. no apostrophe needed! User entered `2.14`
7. Next prompt indicated the new calibration factor saved to the Arduino memory, followed by new scale reading after calibration.
8. Calibration is complete and the Serial monitor keeps showing new lines of data.
9. In order to calibrate the scale on port 6, enter `c` in the message panel again and choose port 6.

### 2. Edit config file
Open the `Acoustic Chambers Environment Control` folder. Click on the `config_files` folder and open the relevant config file for editing (If not familiar, read [how to use the config file](https://github.com/NeuralSyntaxLab/acoustic_chamber_environment_control/blob/46e9405cdcb7c96c5ceae5696ab63bdf03effe7b/config_files/How%20to%20use%20the%20config%20file.md) for more information).

Here, you will need to enter the names of the birds that have weighing devices in their cage in the `Channels` section.
Each docking point (channel) is connected to one scale. Write the name of the bird that connected to each channel with apostrophes.
You also need to make sure the the `scaleDataReadingAndSaving` has the input of **1**, and that the `scaleOutputBasePath` is correct.
At last, enter the time of day you wish to get the daily weight reports sent to the lab's `monitor_alerts` channel. 

For example - `channel1: 'lr17'`, send reports daily at 12:05PM

Example 1

### 3. Re-run the main control script
After calibrating the scales and updating the config file, the system is ready to go.
In order to run the main control script, simply reboot the minicomputer. The script should run automatically at startup.

* It is recommended to test the system to see that it works properly before leaving it to run. You can run the script by opening the `Acoustic Chambers Environment Control` folder, and double clicking the `startup_script.sh` script and choose to execute it (not in terminal) when prompted.
* You can also open the terminal and run the following comand (Change paths accordingly):
```
python /path/to/script/main_control.py --config=/path/to/config/file
```

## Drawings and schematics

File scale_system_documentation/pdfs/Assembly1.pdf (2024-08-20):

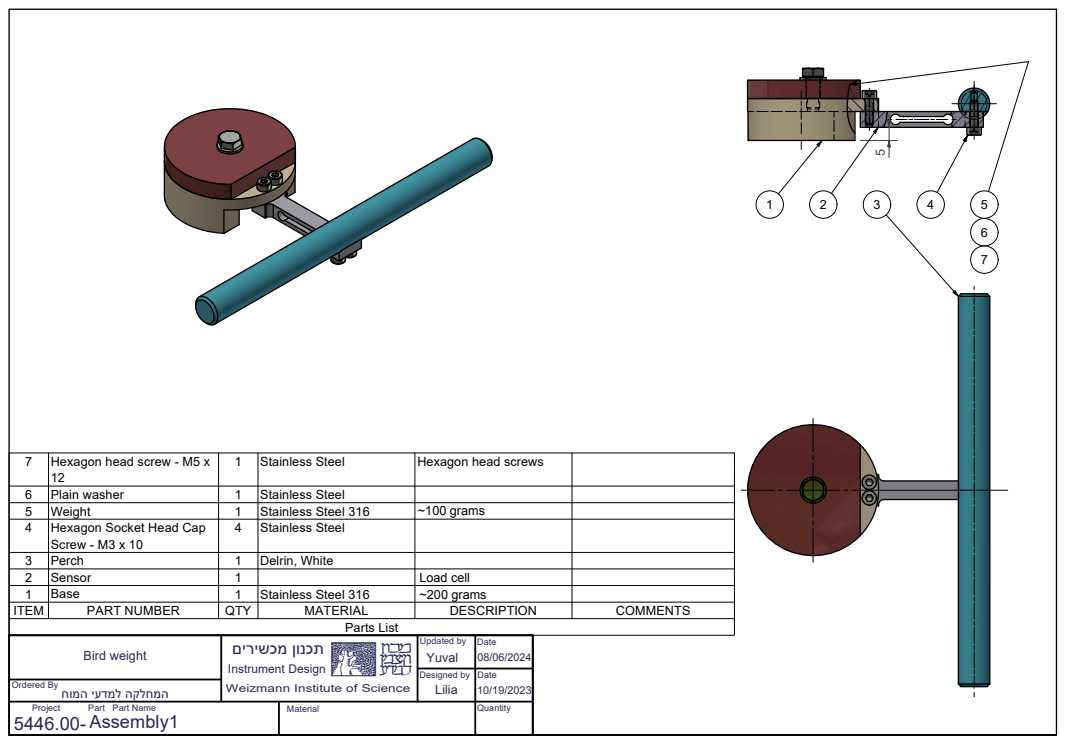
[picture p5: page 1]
Parts List

7 | Hexagon head screw - M5 x 12 | 1 | Stainless Steel | Hexagon head screws

6 | Plain washer | 1 | Stainless Steel
5 | Weight | 1 | Stainless Steel 316 | ~100 grams
4 | Hexagon Socket Head Cap Screw - M3 x 10 | 4 | Stainless Steel

3 | Perch | 1 | Delrin, White
2 | Sensor | 1 | | Load cell
1 | Base | 1 | Stainless Steel 316 | ~200 grams
ITEM | PART NUMBER | QTY | MATERIAL | DESCRIPTION | COMMENTS

Bird weight | Instrument Designzx תכנון מכשירים | Updated by Yuval | Date 08/06/2024

Designed by Lilia | Date 10/19/2023

Weizmann Institute of Science Ordered By

המחלקה למדעי המוח

Project Part Part Name 5446.00- Assembly1 | Material | Quantity

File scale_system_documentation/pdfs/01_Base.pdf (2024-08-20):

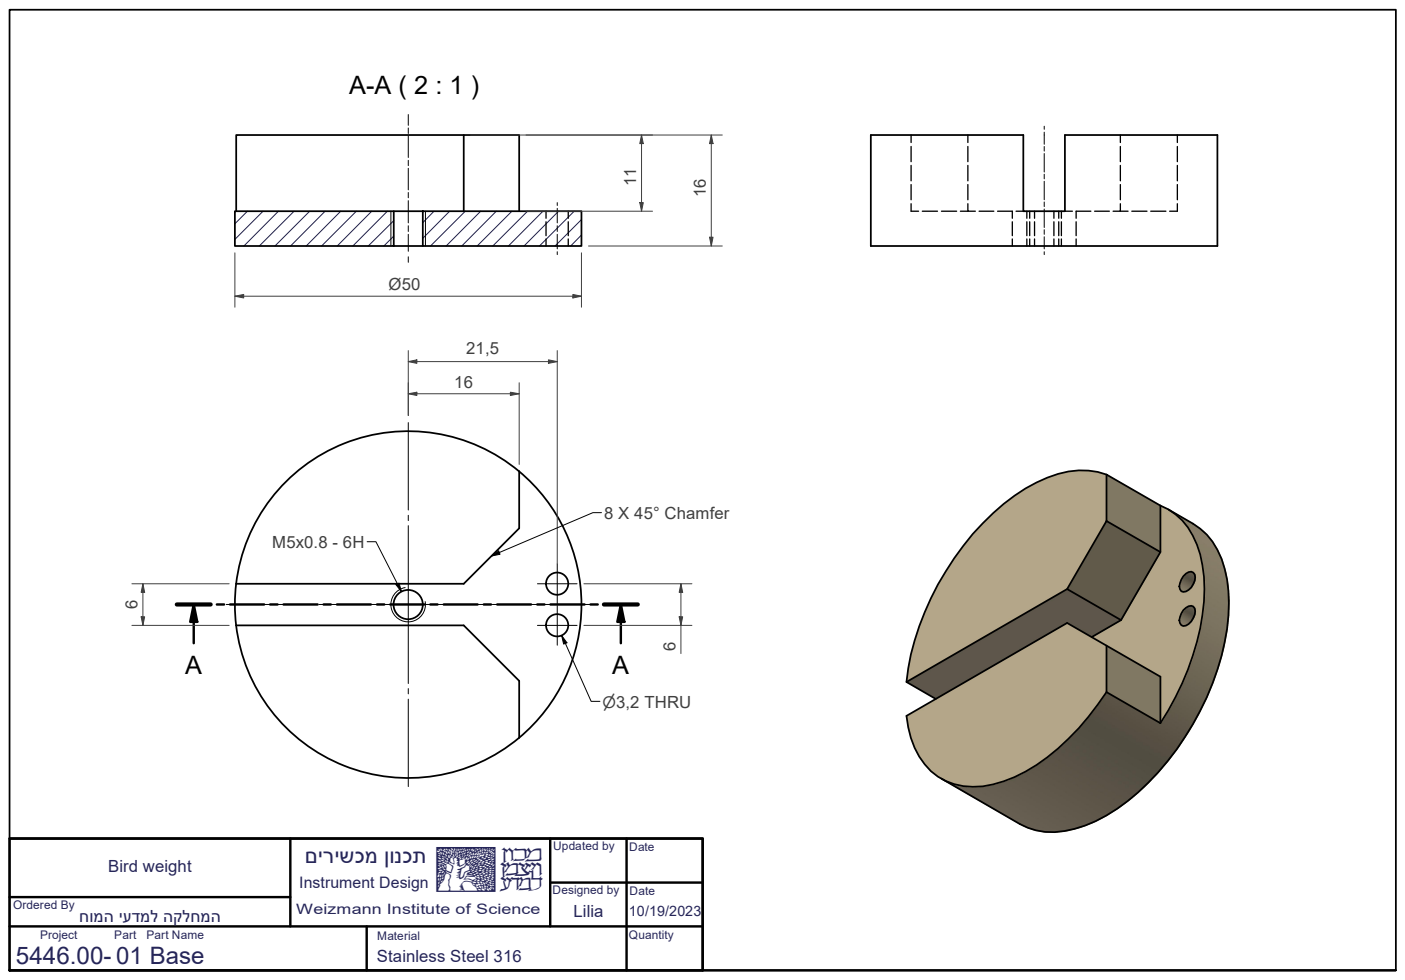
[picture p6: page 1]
Ordered By; ⌀3,2 THRU; 8 X 45° Chamfer

Bird weight | Instrument Designzx תכנון מכשירים Weizmann Institute of Science | Updated by | Date

Designed by Lilia | Date 10/19/2023

המחלקה למדעי המוח

Project Part Part Name 5446.00-01 Base | Material Stainless Steel 316 | Quantity

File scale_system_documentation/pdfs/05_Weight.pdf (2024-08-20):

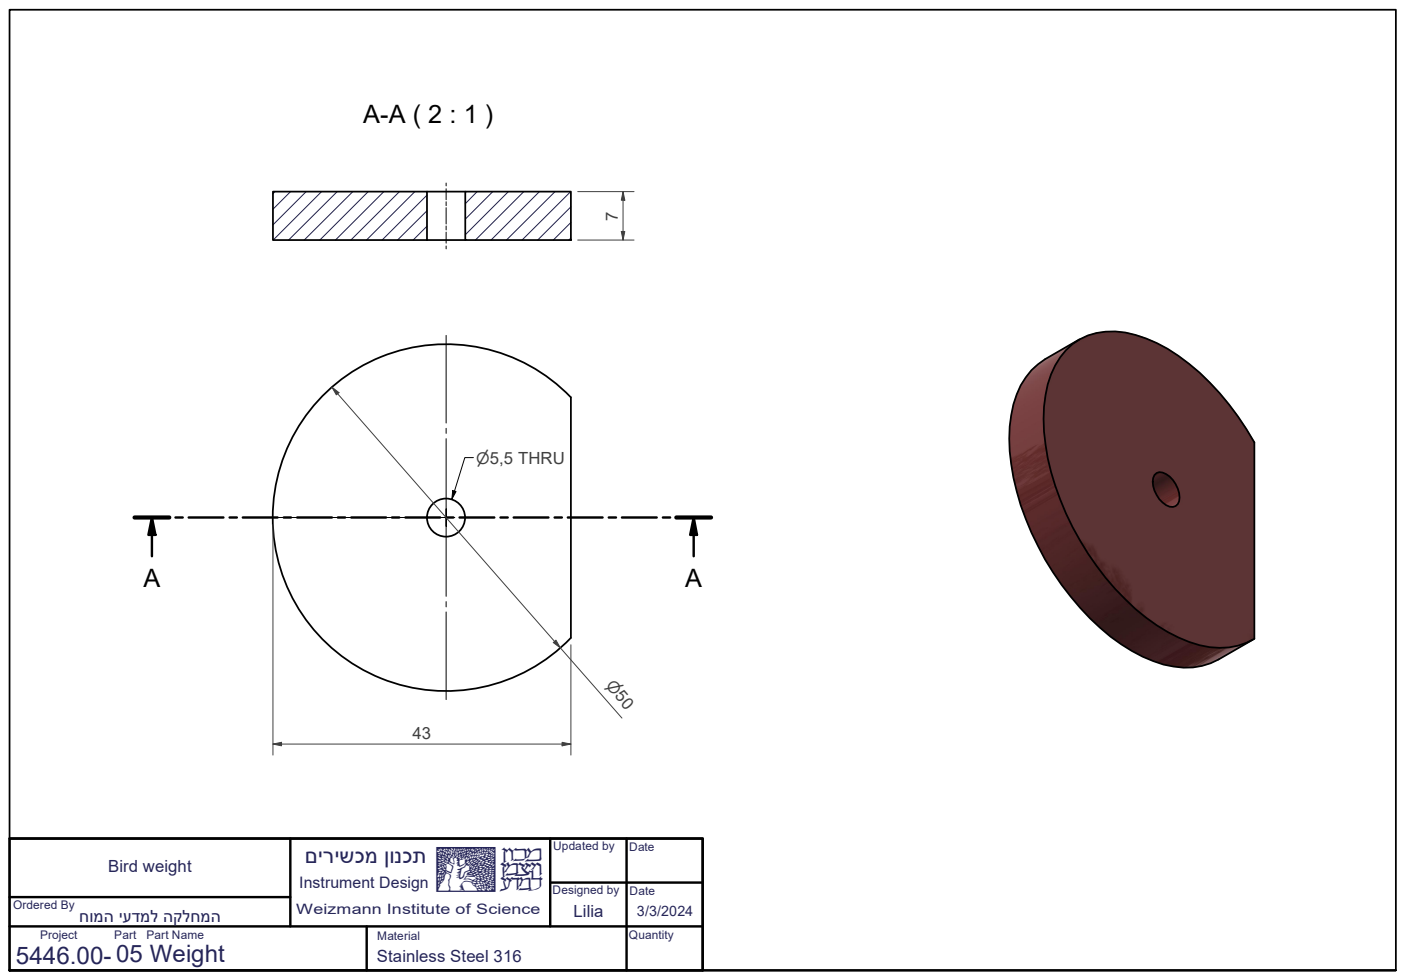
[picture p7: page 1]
Ordered By; ⌀5,5 THRU

Bird weight | Instrument Designzx תכנון מכשירים Weizmann Institute of Science | Updated by | Date

Designed by Lilia | Date 3/3/2024

המחלקה למדעי המוח

Project Part Part Name 05 Weight 5446.00- | Material Stainless Steel 316 | Quantity

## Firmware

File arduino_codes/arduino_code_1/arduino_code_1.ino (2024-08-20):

/***************************************************************************
* THIS IS THE MAIN ARDUINO CODE FOR ACOUSTIC CHAMBERS LIGHT CYCLE CONTROL, AS WELL AS SENSOR(DHT+LIGHT) & WEIGHT DATA ACQUISITION

* It has two functionalities -
*   1. Turn the lights on/off, based on an input from the serial port.
*       Data from the serial port arrives as an int, and so we set a
*       threshold to decide whether the light goes on or off.
*
*   2. Read data from temp. and humidity sensors, as well as light and weight
*     sensors, and print values to the serial port (via Serial.print()).
*     This data will later be read by our Raspberry Pi device, whenever
*     we're ready to consume the data.

NOTE: PLEASE MAKE SURE THAT THE FOLLOWING LIBRARY IS INSTALLED IN ARDUINO IDE:
SparkFun I2C Mux Arduino Library

***************************************************************************/

#include <dht.h>
#include <Wire.h>
#include <EEPROM.h> //Needed to record user settings
#include <SparkFun_I2C_Mux_Arduino_Library.h>
#include <SparkFun_Qwiic_Scale_NAU7802_Arduino_Library.h>

#define DHT22_PIN 8
QWIICMUX myMux;
NAU7802 myScale;
dht DHT;

//EEPROM locations to store 20-byte variables
#define LOCATION_CALIBRATION_FACTOR(port) (port * 20) // Float, requires 4 bytes, plus extra space.
#define LOCATION_ZERO_OFFSET(port) (LOCATION_CALIBRATION_FACTOR(port) + 8) // //Must be more than 4 away from previous spot. Long, requires 4 bytes of EEPROM
bool settingsDetected = false; //Used to prompt user to calibrate their scale

const int numScales = 8; // Number of Qwiic Scale ports available

int LIGHT_SWITCH_PIN = 13;
int BYTES_THRESHOLD = 100;
int incomingByte = 0; // Variable that will contain user input

int ldrPin = A0;
unsigned long seconds = 1000L;
unsigned long minutes = seconds * 1;
unsigned long DelayRate = minutes;

void setup() {
  pinMode(LIGHT_SWITCH_PIN, OUTPUT);
  pinMode(ldrPin, INPUT);
  Wire.begin();

  Serial.begin(9600);

  // myScale setup and scale parameters acquisition
  if (!myMux.begin()) {
  Serial.println("Mux not detected. Make sure scale system is connected properly and try again. Swich to arduino_code_0 to monitor DHT data alone, or to arduino_code_2 to test and calibrate scale.");
  delay(DelayRate);
  }
  else {
  Serial.println("Mux detected");
  
  for (int i = 0; i < numScales; ++i) {
    myMux.enablePort(i);
    myScale.begin();

    if (myScale.begin()) {

      myScale.setSampleRate(NAU7802_SPS_320); //Increase to max sample rate
      myScale.calibrateAFE(); //Re-cal analog front end when we change gain, sample rate, or channel 
    }
    myMux.disablePort(i);
  } 
  } 
}

void loop() {

  //This part is for DHT data acquisition and printing out of all the data
  int LDRinput = analogRead(ldrPin);
  int chk = DHT.read22(DHT22_PIN);

  switch (chk) {
    case DHTLIB_OK:
      break;
    case DHTLIB_ERROR_CHECKSUM:
      Serial.print(0);
      break;
    case DHTLIB_ERROR_TIMEOUT:
      Serial.print(0);
      break;
    default:
      Serial.print(0);
      break;
  }
  
  Serial.print(DHT.humidity);
  Serial.print(";");
  Serial.print(DHT.temperature);
  Serial.print(";");
  Serial.print(LDRinput);
  Serial.print(";");

  if (Serial.available() > 0) {
    incomingByte = Serial.read();
    if (incomingByte > BYTES_THRESHOLD) {
      digitalWrite(LIGHT_SWITCH_PIN, HIGH);
    } else {
      digitalWrite(LIGHT_SWITCH_PIN, LOW);
    }
  }
  // This part is for acquisition of data from all connected scales
  for (int i = 0; i < numScales; ++i) {
    myMux.setPort(i); // Activate communication with active scale #[i], disable all other ports
 
    if (myScale.available() == true) {
      readSystemSettings(i);
      float currentScaleReading = myScale.getWeight();
      if (!isnan(currentScaleReading)) {
        Serial.print(currentScaleReading, 2);
        Serial.print(";");   
      } else {
        Serial.print(0);
        Serial.print(";");
      } 
    } 
    else {
      Serial.print(0);
      Serial.print(";");
    }
  }
  Serial.println("");
  myMux.setPort(-1); // disable all ports

  delay(DelayRate); //wait 1 second until next data reading

}

//Scale functions for communicating with EEPROM(non-vlatile memory of arduino)

//Reads the current system settings from EEPROM
//If anything looks weird, reset setting to default value
void readSystemSettings(int scalePort) //REQUIRED to read an already-calibrated system settings (zero offset and calibration factor)
{
  float settingCalibrationFactor; //Value used to convert the load cell reading to lbs or kg
  long settingZeroOffset; //Zero value that is found when scale is tared

  //Look up the calibration factor
  EEPROM.get(LOCATION_CALIBRATION_FACTOR(scalePort), settingCalibrationFactor);
  if (settingCalibrationFactor == 0xFFFFFFFF)
  {
    settingCalibrationFactor = 0; //Default to 0
    EEPROM.put(LOCATION_CALIBRATION_FACTOR(scalePort), settingCalibrationFactor);
  }

  //Look up the zero tare point
  EEPROM.get(LOCATION_ZERO_OFFSET(scalePort), settingZeroOffset);
  if (settingZeroOffset == 0xFFFFFFFF)
  {
    settingZeroOffset = 1000L; //Default to 1000 so we don't get inf
    EEPROM.put(LOCATION_ZERO_OFFSET(scalePort), settingZeroOffset);
  }

  //Pass these values to the library
  myScale.setCalibrationFactor(settingCalibrationFactor);
  myScale.setZeroOffset(settingZeroOffset);

  settingsDetected = true; //Assume for the moment that there are good cal values
  if (settingCalibrationFactor < 0.1 || settingZeroOffset == 1000)
    settingsDetected = false; //Defaults detected. Prompt user to cal scale.
}

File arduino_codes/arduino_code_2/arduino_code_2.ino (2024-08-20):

/***************************************************************************
* THIS IS THE MAIN ARDUINO CODE FOR CALIBRATING THE SCALE SYSTEM

* It can be used to calibrate new scales or re-calibrate existing scales.

* In order to use it:
* 1. Stop the main code running on the Raspi
* 2. Upload this version of the arduino code on the arduino UNO.
* 3. If needed, connect / disconnect new scales to the system
* 4. Follow the instructions on the Serial monitor

NOTE: PLEASE MAKE SURE THAT THE FOLLOWING LIBRARY IS INSTALLED IN ARDUINO IDE:
SparkFun I2C Mux Arduino Library

Software explanations and information:

EEPROM main functions:  (for more information visit https://docs.arduino.cc/learn/built-in-libraries/eeprom/)
EEPROM is a sort of internal storage of the arduino (non-volatile memory - NVM).
It has 1024 bytes (in UNO) for storage and can endure up to 100,000 write/erase instances.
For the calibration of the scale we use this storage, in order to store the calibration factor and zero offset of each scale.
here are some modules and their meaning:
LOCATION_CALIBRATION_FACTOR(port) - used to define the location of each port's calibration factor
LOCATION_ZERO_OFFSET(port) - used to define the location of each port's zero offset
   The locations are based on the storage requirements of the data with extra space taken for future alterations, total 20 bytes:
     - Each port takes the first 20 spots after the 20*portNumber
     - First 4 bytes for float (calibration factor)
     - 4 bytes extra space
     - 4 bytes for long (zero offset)
     - 8 bytes extra space
EEPROM.get(adress, variable) - receives the data stored in (adress) to (variabe)
EEPROM.put(adress, data) - sets a new value (data) to the defined adress (adress)

NAU7802 main functions: (for more information visit the SparkFun_Qwiic_Scale_NAU7802_Arduino_Library - src folder )
myScale.calculateCalibrationFactor() - Sets the calibration factor based on the weight on scale and zero offset.
myScale.calculateZeroOffset() - Also called taring. Call this with nothing on the scale
myScale.getCalibrationFactor() - Ask library for this value. Useful for storing value into NVM.
myScale.getZeroOffset() - Ask library for this value. Useful for storing value into NVM.
myScale.setCalibrationFactor() - ass a known calibration factor into library. Helpful if users is loading settings from NVM.
myScale.setZeroOffset() - Sets the internal variable. Useful for users who are loading values from NVM.\
***************************************************************************/


#include <EEPROM.h> //Needed to record user settings
#include <SparkFun_I2C_Mux_Arduino_Library.h>
#include "SparkFun_Qwiic_Scale_NAU7802_Arduino_Library.h"

QWIICMUX myMux;
NAU7802 myScale;


//EEPROM locations to store 20-byte variables
#define LOCATION_CALIBRATION_FACTOR(port) (port * 20) // Float, requires 4 bytes, plus extra space.
#define LOCATION_ZERO_OFFSET(port) (LOCATION_CALIBRATION_FACTOR(port) + 8) // //Must be more than 4 away from previous spot. Long, requires 4 bytes of EEPROM
bool settingsDetected = false; //Used to prompt user to calibrate their scale

const int numScales = 8; // Number of Qwiic Scale ports available

int incomingByte = 0; // Variable that will contain user input

unsigned long seconds = 1000L;
unsigned long minutes = seconds * 1;
unsigned long DelayRate = minutes;

void setup() {

  Wire.begin();

  Serial.begin(9600);

  //myScale setup and scale parameters acquisition / calibration
  if (!myMux.begin()) {
  Serial.println("Mux not detected. Freezing...");
  while (1);
  }
  Serial.println("Mux detected");

  for (int i = 0; i < numScales; ++i) {
    myMux.enablePort(i);
    myScale.begin();
    delay(1);

    if (!myScale.begin()) {
      Serial.println("No scale detected on port " + String(i));
    } 
    else {
      Serial.println("Scale detected on port " + String(i));
      
      myScale.setSampleRate(NAU7802_SPS_320); //Increase to max sample rate
      myScale.calibrateAFE(); //Re-cal analog front end when we change gain, sample rate, or channel 

      readSystemSettings(i); //Load zeroOffset and calibrationFactor from EEPROM
      if(settingsDetected == false) {
        Serial.print("\tScale " + String(i));
        //Serial.print(i);
        Serial.println(" not calibrated. Follow calibration instructions.");
        // Serial.print(" not calibrated. Calibrating scale:");

        // calibrateScale();
      } 
      else {
        Serial.print("Zero offset: ");
        Serial.println(myScale.getZeroOffset());
        Serial.print("Calibration factor: ");
        Serial.println(myScale.getCalibrationFactor());
      }
    }
    myMux.disablePort(i);
  } 
}

void loop() {

  for (int i = 0; i < numScales; ++i) {

    myMux.setPort(i); // Activate communication with active scale #[i], disable all other ports
    Serial.print(" c"); 
    Serial.print(i);
    Serial.print(": "); // indicate channel number before each value
    
    // for every port, check if there is a new scale reading and print it. If no input from the scale print 0.
    if (myScale.available() == true) {
      readSystemSettings(i);
      float currentScaleReading = myScale.getWeight();
      if (!isnan(currentScaleReading)) {
      Serial.print(currentScaleReading, 2);
      Serial.print(";");   
      } else {
        Serial.print(0);
        Serial.print(";");
      } 
    } 
    else {
      Serial.print(0);
      Serial.print(";");
    }

  }
  Serial.println("");
  myMux.setPort(-1); // disable all ports


  if (Serial.available() > 0) {
    incomingByte = Serial.read();
    if (incomingByte == 't') //Tare the scale
    {
      tareScale();
    }
    else if (incomingByte == 'c') //Calibrate
    {
      calibrateScale();
    }
    else if (incomingByte == 's') // Show system settings of connected scales
    {
      showScaleSettings();
    }
  }
  delay(DelayRate);
}


//Weight sensor Calibration and EEPROM(non-vlatile memory of arduino) stuff

//Gives user the ability to set a known weight on the scale and calculate a calibration factor
void calibrateScale()
{
  int selectedPort = -1; // Initialize selectedPort with an invalid value

  while (selectedPort < 0 || selectedPort >= numScales) {
    Serial.println("Enter scale port number to calibrate (0-7): ");
    while (Serial.available()) Serial.read(); //Clear anything in RX buffer
    while (Serial.available() == 0) delay(10); //Wait for user to press key
    selectedPort = Serial.parseInt();
    
    // Check if the input is within the valid range and corresponds to an active scale
    if (selectedPort < 0 || selectedPort >= numScales) {
      Serial.println("Invalid scale port number. Please enter a number between 0 and 7 for an active scale.");
    }
  }

  // at this point, selectedPort is a valid port number. Proceeding with calibration process
  myMux.setPort(selectedPort);
  Serial.println();
  Serial.println("Starting calibration for scale on port " + String(selectedPort));
  

  Serial.println(F("Setup scale with no weight on it. Press a key when ready."));
  while (Serial.available()) Serial.read(); //Clear anything in RX buffer
  while (Serial.available() == 0) delay(10); //Wait for user to press key

  myScale.calculateZeroOffset(64); //Zero or Tare the scale. Average over 64 readings. This command also sets the new zero offset temporarily in myScale object until arduino is shut down or new value is acquired.
  Serial.print(F("New zero offset: "));
  Serial.println(myScale.getZeroOffset());

  Serial.println(F("Place known weight on scale. Press a key when weight is in place and stable."));
  while (Serial.available()) Serial.read(); //Clear anything in RX buffer
  while (Serial.available() == 0) delay(10); //Wait for user to press key

  Serial.print(F("Please enter the weight, without units, currently sitting on the scale (for example '4.25'): "));
  while (Serial.available()) Serial.read(); //Clear anything in RX buffer
  while (Serial.available() == 0) delay(10); //Wait for user to press key

  //Read user input
  float weightOnScale = Serial.parseFloat();
  Serial.println();

  myScale.calculateCalibrationFactor(weightOnScale, 64); //Tell the library how much weight is currently on it and will also set the new calibration factor temporarily in myScale object.
  Serial.print("Scale " + selectedPort);
  Serial.print(" Calibrated. New cal factor: ");
  Serial.println(myScale.getCalibrationFactor(), 2);

  Serial.print(F("New Scale Reading: "));
  Serial.println(myScale.getWeight(), 2);

  recordSystemSettings(selectedPort); //Commit these values to EEPROM 
  myMux.disablePort(selectedPort);
}
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

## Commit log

2024-08-20 Upload updated version of the environment control project to GIT
    [Assembly1.stp, parts list.xlsx]
2025-07-16 Update Raspberry Pi Configuration.md
    Remove noauto from 'sudo nano /etc/fstab' command line for automatic mounting STORWIS using mount-a
